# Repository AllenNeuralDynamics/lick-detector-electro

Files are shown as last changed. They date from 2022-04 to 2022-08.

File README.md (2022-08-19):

# Lick Detector Electro

This is a migration of the [Dual Lick Port](https://www.janelia.org/open-science/dual-lick-port-detector)
from [Janelia Research Campus](https://www.janelia.org/).

## Device Overview

The Dual Lick Port uses a [two-transistor amplifier circuit](https://www.electronics-notes.com/articles/analogue_circuits/transistor/amplifier-npn-pnp-two-transistor-circuit.php)
to detect licks from an instrumented lick port where the mouse receives liquids.
This detection circuit can be operated isolated or non-isolated from the output
signal made available on each Lick Port.

Lick Ports can be plugged directly into a a Harp Behavior Device Port as-is
with a CAT6 cable.

This board also exposes each Lick Port's 12V output via the two Molex Microfit
3 sockets on the top-and-bottom right side of the board.

## Connection Overview
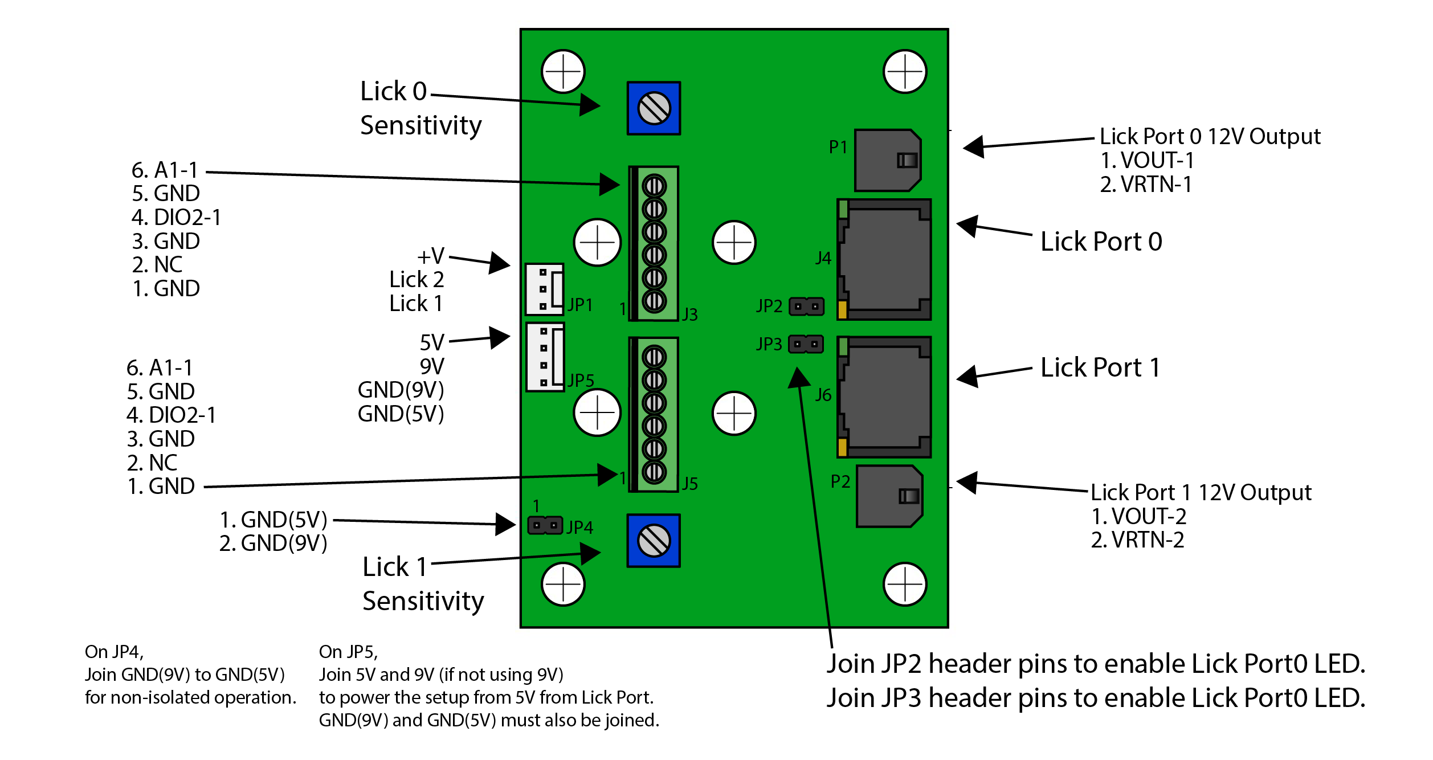
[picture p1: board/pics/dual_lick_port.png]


## Schematic

[schematic.pdf](./board/JF-SV-LP0001.pdf)

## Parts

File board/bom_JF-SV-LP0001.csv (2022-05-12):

Schematic Component | Circuit Component | Part Number from Digi-Key | Quantity | Cost/ | Cost Total
JP2, JP3, JP4 | 2 Pin Header | 609-3506-ND | 3 | $0.26 | $0.78 | 30
P1, P2 | 2 Pin Connector | WM1860-ND | 2 | $0.84 | $1.68 | 20
JP1 | 3 Pin Header | WM4201-ND | 1 | $0.30 | $0.30 | 10
JP5 | 4 Pin Header | WM4202-ND | 1 | $0.37 | $0.37 | 10
J4, J6 | RJ45 with LEDs | RJHSE-3081-ND | 2 | $2.54 | $5.08 | 20
J3, J5 | TERM BLOCK 6POS SIDE ENT 3.5MM | A98162-ND | 2 | $2.67 | $5.34 | 20
OK1, OK2 | OPTOCOUPLER TRANS-OUT 6-SMD | 4N25SM-ND | 2 | $0.57 | $1.14 | 20
R1, R12 | Resistor, 150 ohms, 1%, 0805 | P150CCT-ND | 2 | $0.10 | $0.20 | 20
R2, R13 | Resistor, 1.0K, 1%, 0805 | 541-1.00KCCT-ND | 2 | $0.10 | $0.20 | 20
R9, R20 | Resistor, 499 ohms, 1%, 0805 | 541-499CCT-ND | 2 | $0.10 | $0.20 | 20
R6, R7, R8, R17, R18, R19 | Resistor, 100K, 1%, 0805 | P100KCCT-ND | 6 | $0.10 | $0.60 | 60
R4, R5, R15, R16 | Resistor, 10.0M, 1%, 0805 | 541-10.0MCCT-ND | 4 | $0.10 | $0.40 | 40
R11, R22 | Resistor, 10.0K, 1%, 0805 | 541-10.0KCCT-ND | 2 | $0.10 | $0.20 | 20
R10, R21 | Trim Pot, 100K, top adjust | 3386P-104LF-ND | 2 | $1.24 | $2.48 | 20
Q1, Q3 | TRANS NPN 40V 200MA SOT23 | 568-4510-1-ND | 2 | $0.14 | $0.28 | 20
Q2, Q4 | TRANSISTOR GP PNP AMP SOT-23 | MMBT3906FSCT-ND | 2 | $0.17 | $0.34 | 20
Shunt Jumpers (as required) | 2 pos, 0.1” center | A26242-ND | 4 | $0.31 | $1.24 | 40
PCB |  |  | 1 | $14.58 | $14.58
 |  |  |  |  | $35.41

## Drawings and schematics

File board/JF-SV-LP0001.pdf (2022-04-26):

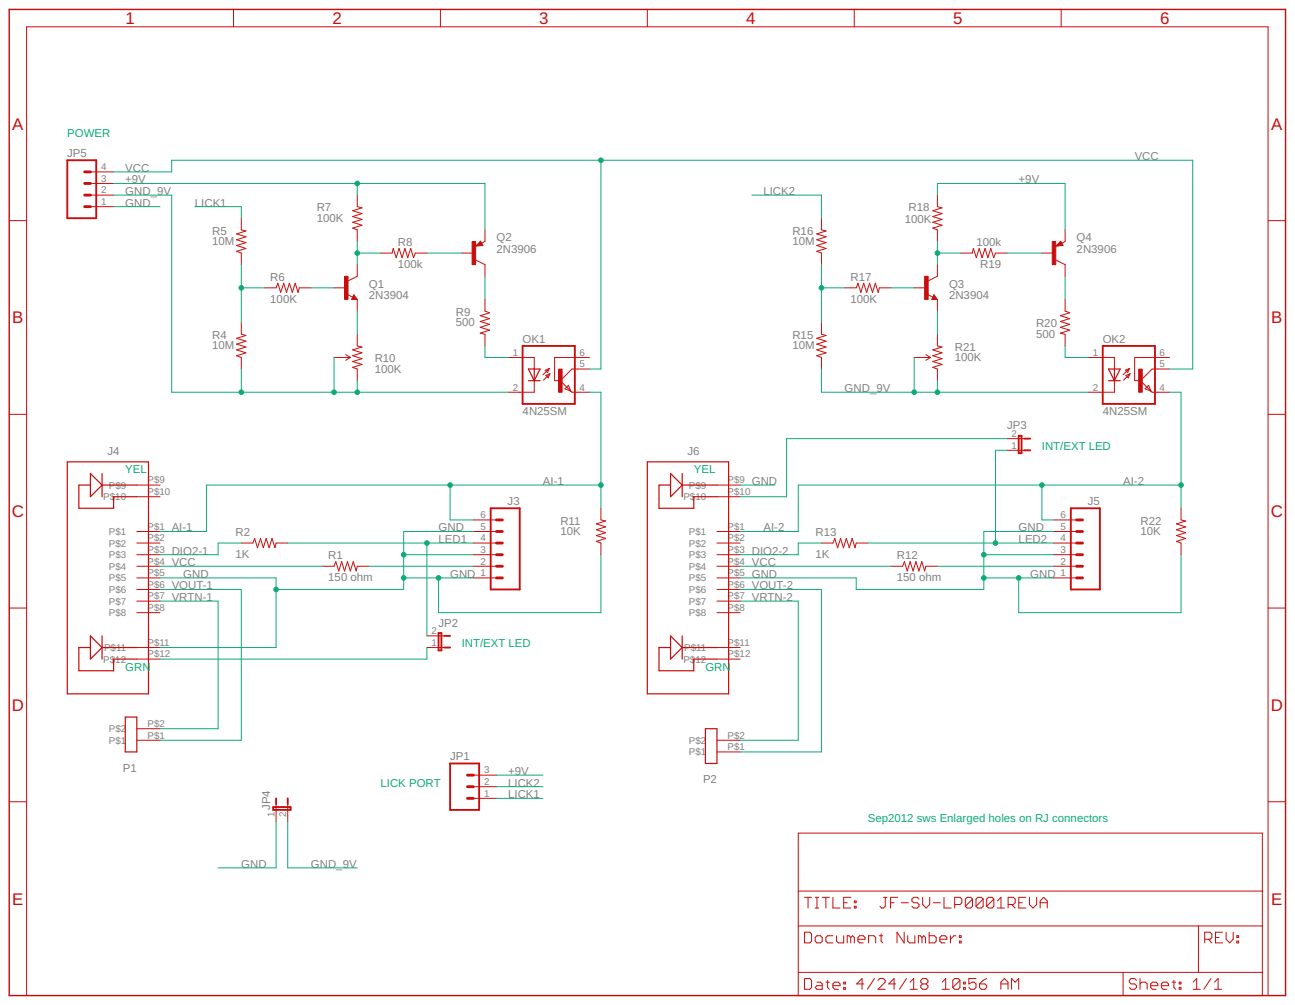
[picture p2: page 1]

Sep2012 sws Enlarged holes on RJ connectors

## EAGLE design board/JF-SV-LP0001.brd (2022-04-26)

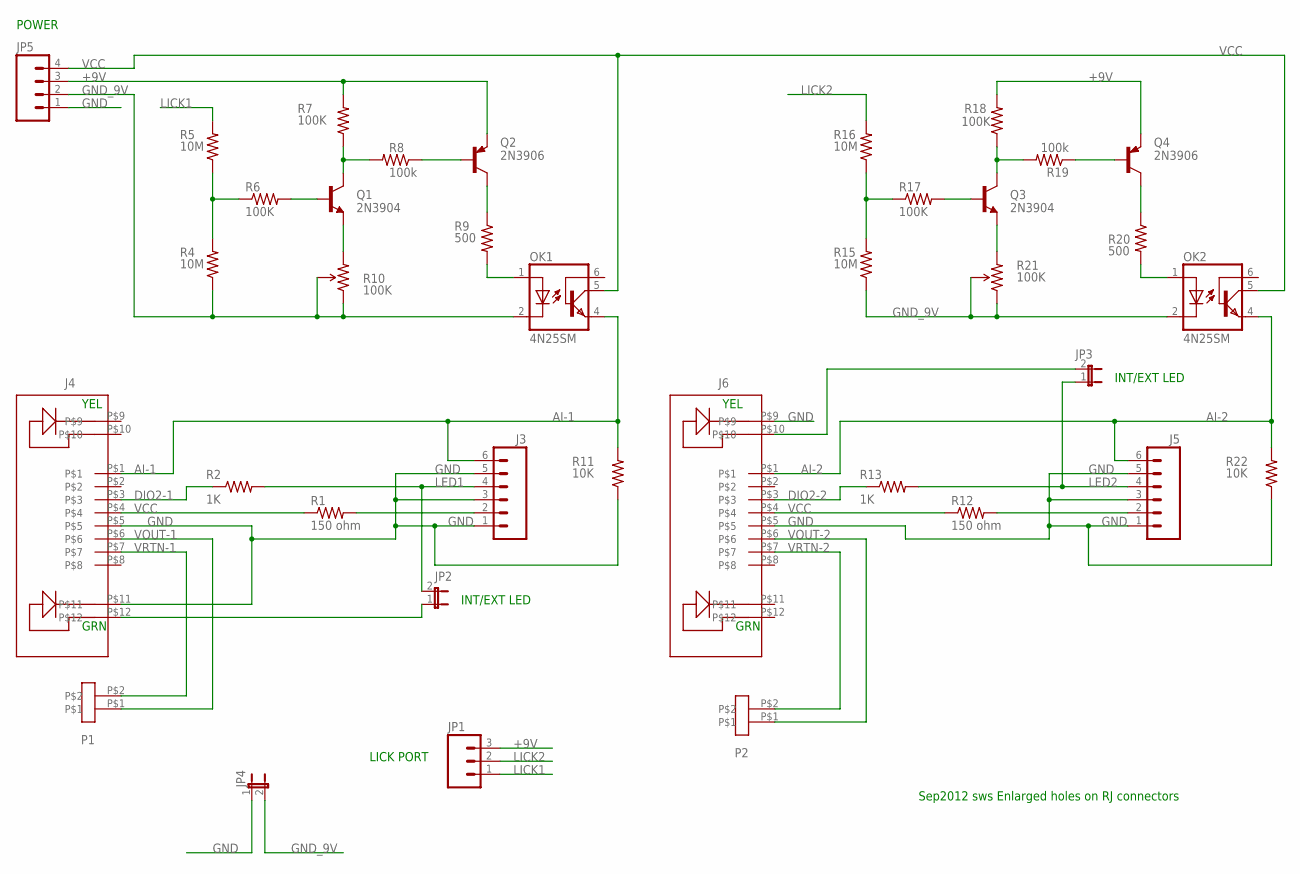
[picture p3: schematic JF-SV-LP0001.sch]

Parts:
J3, J5: M063.5MM-6; SCREWTERMINAL-3.5MM-6
J4, J6: RJ45_LED
JP1: M03POLAR; MOLEX-1X3
JP2, JP3: JP1E; JP1
JP4: JUMPER-2PTH; 1X02
JP5: M04POLAR; MOLEX-1X4
OK1, OK2: 4N25SM; DIL6-SMD
P1, P2: CON2MICRO-FIT; MICRO-FIT-2-RA
Q1, Q3: 2N3904; SOT23-BEC
Q2, Q4: 2N3906; SOT23-BEC
R1, R12: 150 ohm; 0805S
R2, R13: 1K; 0805S
R4, R5, R15, R16: 10M; 0805S
R6, R7, R17, R18: 100K; 0805S
R8, R19: 100k; 0805S
R9, R20: 500; 0805S
R10, R21: 100K; TRIM_POT_PTH
R11, R22: 10K; 0805S

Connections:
+9V: JP1.3, JP5.3, Q2.E, Q4.E, R7.2, R18.2
AI-1: J3.6, J4.P$1, OK1.4 (EMI), R11.2
AI-2: J5.6, J6.P$1, OK2.4 (EMI), R22.2
DIO2-1: J4.P$3, R2.1
DIO2-2: J6.P$3, R13.1
GND: J3.1, J3.3, J3.5, J4.P$5, J4.P$11, J5.1, J5.3, J5.5, J6.P$5, J6.P$9, JP4.1, JP5.1, R11.1, R22.1
GND_9V: JP4.2, JP5.2, OK1.2 (C), OK2.2 (C), R4.1, R10.1 (CCW), R10.2 (WIPER), R15.1, R21.1 (CCW), R21.2 (WIPER)
LED1: J3.4, JP2.2, R2.2
LED2: J5.4, JP3.1, R13.2
LICK1: JP1.1, R5.2
LICK2: JP1.2, R16.2
unnamed: J3.2, R1.2
unnamed: OK1.1 (A), R9.2
unnamed: J4.P$12, JP2.1
unnamed: R4.2, R5.1, R6.1
unnamed: Q1.B, R6.2
unnamed: Q1.E, R10.3 (CW)
unnamed: Q1.C, R7.1, R8.2
unnamed: Q2.B, R8.1
unnamed: Q2.C, R9.1
unnamed: J6.P$10, JP3.2
unnamed: J5.2, R12.2
unnamed: R15.2, R16.1, R17.1
unnamed: Q3.B, R17.2
unnamed: Q3.E, R21.3 (CW)
unnamed: Q3.C, R18.1, R19.2
unnamed: Q4.B, R19.1
unnamed: OK2.1 (A), R20.2
unnamed: Q4.C, R20.1
VCC: J4.P$4, J6.P$4, JP5.4, OK1.5 (COL), OK2.5 (COL), R1.1, R12.1
VOUT-1: J4.P$6, P1.P$1
VOUT-2: J6.P$6, P2.P$1
VRTN-1: J4.P$7, P1.P$2
VRTN-2: J6.P$7, P2.P$2

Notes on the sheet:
LICK PORT
POWER
YEL
GRN
INT/EXT LED
Sep2012 sws Enlarged holes on RJ connectors

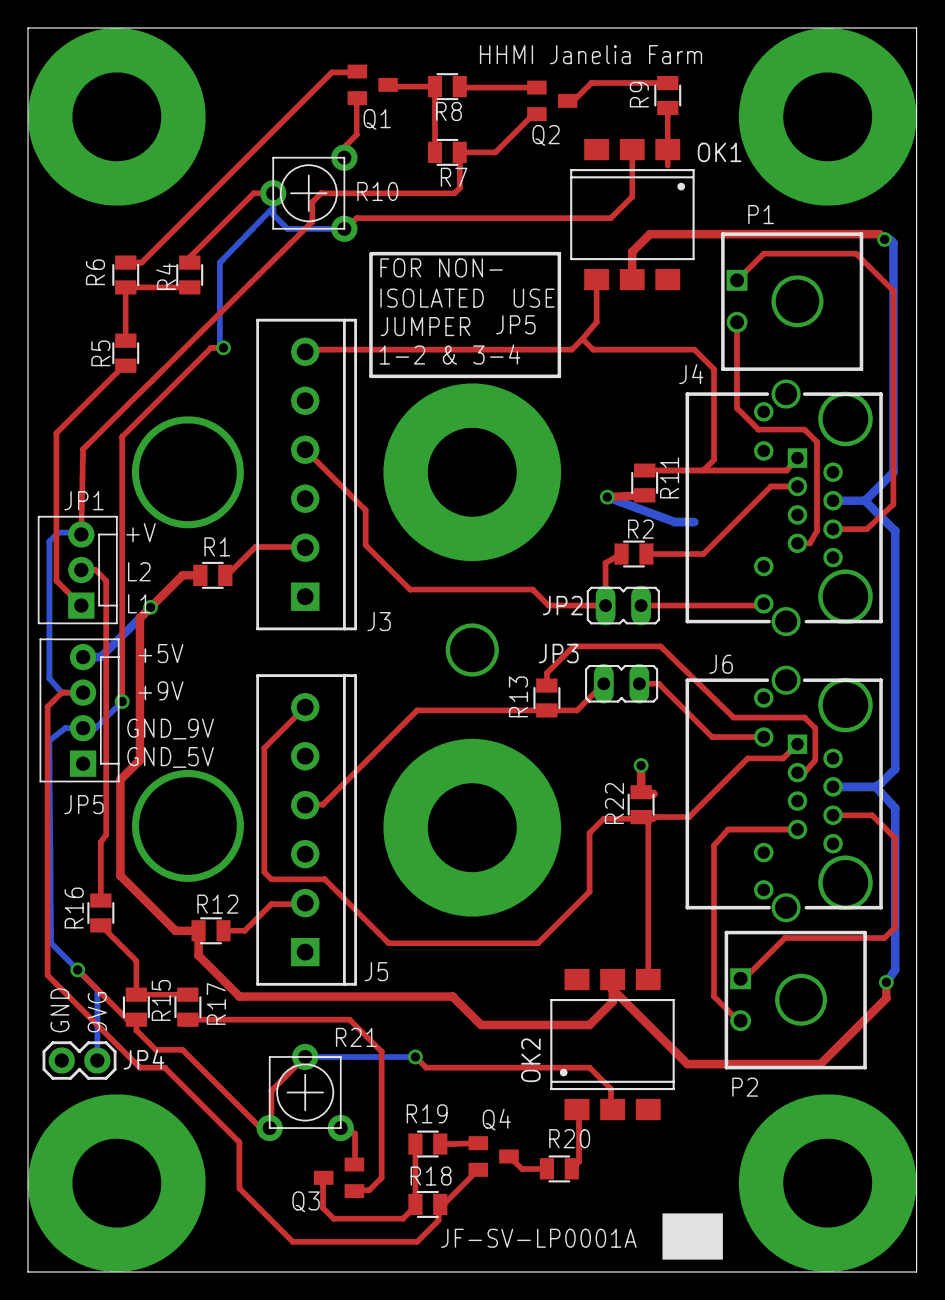
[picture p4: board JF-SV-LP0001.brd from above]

Board: 2 copper layers, 63.5 x 88.9 mm, 37 parts (0 on the bottom side), 34 nets.

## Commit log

2022-04-26 adding board pdf
2022-05-12 convert BOM to CSV
    [JF-SV-LP0001.xlsx, bom_JF-SV-LP0001.csv]
2022-05-12 remove "REVA" from filenames
    We don't know what Rev A is, in relation to the boards that were actually
    produced. Once we produce our own boards, we will mark them with our own
    semantic versioning scheme and tag the applicable commit with that version
    number in this repo.
    [JF-SV-LP0001.brd, JF-SV-LP0001.gbl, JF-SV-LP0001.gbs, JF-SV-LP0001.gtl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]
